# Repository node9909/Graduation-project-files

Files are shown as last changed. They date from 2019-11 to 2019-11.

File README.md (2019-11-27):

# Graduation internship report attachments (HD-SEMG system ADS1298)
 THis folder includes: Hardware files, software files, python application, MATLAB and report, design was to build a protable and wireless HD-SEMG aquisition system for my graduation internship of my electrical engineering degree at Hogeschool Rotterdam, the internship took place at Bio-engineering.pl in Wroclaw.

 The hypothesis of the project was ”Can the AMAC performance level be improved in direct controlled (DC) myoelectric systems by exactly locating the location where the patient has the most amount of cover the agonist and antagonist of the residual limb during different hand gestures’’. The goal was to develop a device that can be used to confirm this hypothesis, the could be achieved by measuring the muscle potentials over the residual limb during different hand gestures (HD-SEMG recording)

 In the project multiple AFE were designed were presented (based on AD8232 adn INA333), the function of the AFE to amplify and filter the EMG signal. THe EMG channels were digitezed using the ADS1298. the ADC data is read from the ADS1298 via an Arduino DUE (SAM3X8E)/ STM32F4.A PC application was developed to visualize the data and verifiy certain system specification (CMRR, IRN and Gain). The Current design is capable of measuring up to 1kSps with the Arduino DUE and to >4kSps with the STM32F411, the problem with the STM32F4 is the the Python application and realterm cannot open the USB port (CDC) to read the data, but it can be open in Tera term. If anybody knows why I would be happy to know :) 

 If you would like to continue this project Idea, feel to contact me for more info about the future improvements or any other questions about the design of the project.

# Contact details
 If you have any questions about the project feel free to contract me at: okersten@gmail.com

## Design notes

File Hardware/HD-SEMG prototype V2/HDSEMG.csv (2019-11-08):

Id | Designator | Behuizing | Hoeveelheid | Orientatie | Leverancier en ref
1 | REF** | KiCad-Logo2_8mm_SilkScreen | 1 | KiCad-Logo2_8mm_SilkScreen
2 | J26,J16,J15,J13,J14,J17,J24 | PinHeader_1x03_P2.54mm_Vertical | 7 | Conn_01x03
3 | GND1 | PinSocket_1x04_P2.54mm_Vertical | 1 | Conn_02x02_Counter_Clockwise
4 | J2 | PinSocket_1x04_P2.54mm_Vertical | 1 | Conn_01x04
5 | J3,J4,J5 | PinSocket_2x02_P2.54mm_Vertical | 3 | Conn_02x02_Counter_Clockwise
6 | J22,J25,J23,J21 | PinSocket_1x03_P2.54mm_Vertical | 4 | Conn_01x03
7 | J10,J9,CH8,CH7,CH6,CH5,CH4 | PinHeader_1x02_P2.54mm_Vertical | 7 | Conn_01x02
8 | J8,J7,J12 | PinHeader_1x01_P2.54mm_Vertical | 3 | Conn_01x01
9 | C54,C56,C55,C53,C52 | C_0805_2012Metric_Pad1.15x1.40mm_HandSolder | 5 | 10uF
10 | J30 | PinHeader_1x08_P2.54mm_Vertical | 1 | Conn_01x08
11 | JP6,JP3,JP1,JP5,JP8,JP9 | PinHeader_1x02_P2.54mm_Vertical | 6 | Jumper
12 | R118,R117,R22,R21,R39,R40 | R_0805_2012Metric_Pad1.15x1.40mm_HandSolder | 6 | 11k
13 | TP4,TP22,TP7,TP21,TP3,TP12,TP20,TP23,TP29,TP25,TP35,TP24,TP1,TP11,TP13,TP14,TP26,TP27,TP28,TP36,TP37,TP6 | keystone_PCB_TEST_PIN | 22 | 5003
14 | U15,U8,U33 | MSOP-8_3x3mm_P0.65mm | 3 | INA333AIDGKR
15 | U9,U35,U17 | VSSOP-8_3.0x3.0mm_P0.65mm | 3 | THS4521IDGKT
16 | R119,R120,R41,R24,R23,R42 | R_0805_2012Metric_Pad1.15x1.40mm_HandSolder | 6 | 50R
17 | U16,U34,U10 | SOT-23-5 | 3 | OPA333xxDBV
18 | R116,R115,R18,R37,R38,R19 | R_0805_2012Metric_Pad1.15x1.40mm_HandSolder | 6 | 5.6k
19 | C1 | C_0805_2012Metric_Pad1.15x1.40mm_HandSolder | 1 | 1M
20 | C4 | C_0805_2012Metric_Pad1.15x1.40mm_HandSolder | 1 | 47nF
21 | C5,C40,C112,C16,C22 | C_0805_2012Metric_Pad1.15x1.40mm_HandSolder | 5 | 4.7uF
22 | J1,J18 | MX387GL | 2 | AUDIO_JACK_By_OLIVER
23 | C6,C48,C120 | C_0805_2012Metric_Pad1.15x1.40mm_HandSolder | 3 | 220nF
24 | C7,C8,C14,C15,C114,C42,C46,C113,C45,C41,C118,C117 | C_0805_2012Metric_Pad1.15x1.40mm_HandSolder | 12 | 100n
25 | C12,C51,C123 | C_0805_2012Metric_Pad1.15x1.40mm_HandSolder | 3 | 33nF
26 | C9,C10,C50,C122 | C_0805_2012Metric_Pad1.15x1.40mm_HandSolder | 4 | 2.2nF
27 | C11,C13,C43,C44,C116,C115 | C_0805_2012Metric_Pad1.15x1.40mm_HandSolder | 6 | 100nF
28 | C49,C121 | C_0805_2012Metric_Pad1.15x1.40mm_HandSolder | 2 | 2.2n
29 | C47,C119 | C_0805_2012Metric_Pad1.15x1.40mm_HandSolder | 2 | 47n
30 | JP4,JP7 | SolderJumper-2_P1.3mm_Open_Pad1.0x1.5mm | 2 | Jumper
31 | R25,R34,R112 | R_0805_2012Metric_Pad1.15x1.40mm_HandSolder | 3 | 220k
32 | R14,R35,R15,R114,R36,R113 | R_0805_2012Metric_Pad1.15x1.40mm_HandSolder | 6 | 1.1k
33 | R17,R31,R108,R109,R16,R30 | R_0805_2012Metric_Pad1.15x1.40mm_HandSolder | 6 | 51k
34 | R20,R110,R32 | R_0805_2012Metric_Pad1.15x1.40mm_HandSolder | 3 | 4300R
35 | R2 | R_0805_2012Metric_Pad1.15x1.40mm_HandSolder | 1 | 1.5nF
36 | R33,R111 | R_0805_2012Metric_Pad1.15x1.40mm_HandSolder | 2 | 430k
37 | R26 | R_0805_2012Metric_Pad1.15x1.40mm_HandSolder | 1 | 110k
38 | R1,R28 | R_0805_2012Metric_Pad1.15x1.40mm_HandSolder | 2 | 100k
39 | TP5,TP2 | TPCW51D250H460P | 2 | 5003
40 | R10 | R_0805_2012Metric_Pad1.15x1.40mm_HandSolder | 1 | 0R
41 | R9,R6,R7 | R_0805_2012Metric_Pad1.15x1.40mm_HandSolder | 3 | 10k
42 | L5,L4,L3,L2 | L_0805_2012Metric_Pad1.15x1.40mm_HandSolder | 4 | INDUCTOR
43 | D1 | D_0805_2012Metric_Castellated | 1 | LED
44 | C2 | Fuse_1812_4532Metric_Pad1.30x3.40mm_HandSolder | 1 | 470pF
45 | C3 | C_1206_3216Metric_Pad1.42x1.75mm_HandSolder | 1 | 2.2uF
46 | C17,C18,C19,C21,C27,C29,C30,C31,C33,C39 | C_0805_2012Metric_Pad1.15x1.40mm_HandSolder | 10 | 1uF
47 | C23,C25,C20 | C_0805_2012Metric_Pad1.15x1.40mm_HandSolder | 3 | 2.2uF
48 | C24,C124 | C_0805_2012Metric_Pad1.15x1.40mm_HandSolder | 2 | 10nF
49 | C26,C28 | C_1206_3216Metric_Pad1.42x1.75mm_HandSolder | 2 | 0.1uF
50 | C32 | C_0805_2012Metric_Pad1.15x1.40mm_HandSolder | 1 | .1uF
51 | C34 | C_0805_2012Metric_Pad1.15x1.40mm_HandSolder | 1 | 22uF
52 | C35 | C_1206_3216Metric | 1 | 10uF
53 | C36 | C_0805_2012Metric_Pad1.15x1.40mm_HandSolder | 1 | 0.1u
54 | C37 | C_0805_2012Metric_Pad1.15x1.40mm_HandSolder | 1 | 1nF
55 | C38 | C_0805_2012Metric_Pad1.15x1.40mm_HandSolder | 1 | 0.1uF
56 | F1 | Fuse_1206_3216Metric_Pad1.42x1.75mm_HandSolder | 1 | Fuse
57 | IC1 | TQFP-64_10x10mm_P0.5mm | 1 | ADS1298_By_Oliver
58 | Power_In1,J31 | TerminalBlock_bornier-2_P5.08mm | 2 | Screw_Terminal_01x02
59 | J11 | BarrelJack_Horizontal | 1 | Barrel_Jack_Switch
60 | L1 | L_Bourns_SRN6045TA | 1 | 10uH
61 | PS1 | CONV_R2S-1205 | 1 | R2S-1205
62 | R3,R4,R5 | R_0805_2012Metric_Pad1.15x1.40mm_HandSolder | 3 | 10K
63 | U11 | SOT-223-3_TabPin2 | 1 | TLV1117-25
64 | U12 | SOT-223-3_TabPin2 | 1 | MCP1825S
65 | U14 | SOT-23-5_HandSoldering | 1 | TPS72325
66 | U36 | SOIC254P1016X460-5N | 1 | 357LB3CI002M0480
67 | R8 | R_0805_2012Metric_Pad1.15x1.40mm_HandSolder | 1 | 50k
68 | U13 | SOIC127P600X175-8N | 1 | MAX889TESA+
69 | U2,U3 | SOIC-16_3.9x9.9mm_P1.27mm | 2 | Si8663
70 | J19 | PinHeader_1x06_P2.54mm_Vertical | 1 | Conn_01x06

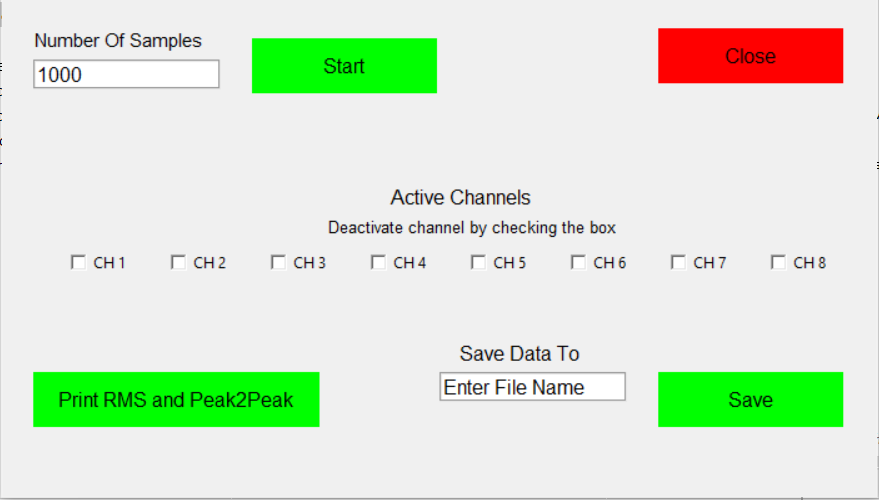
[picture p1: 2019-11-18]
PC Application/app.PNG

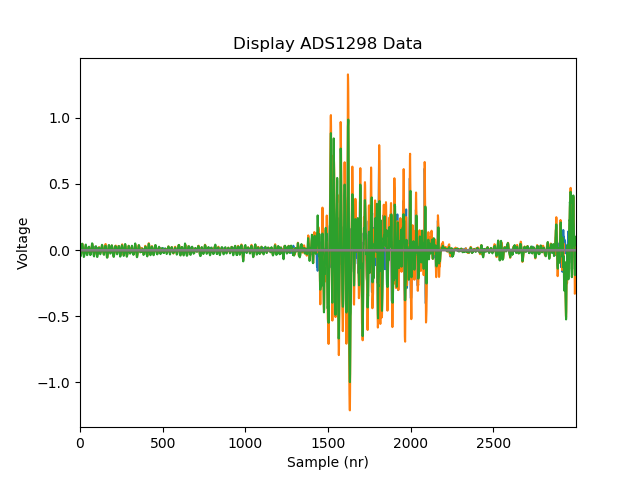
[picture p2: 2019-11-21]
PC Application/realtest.png

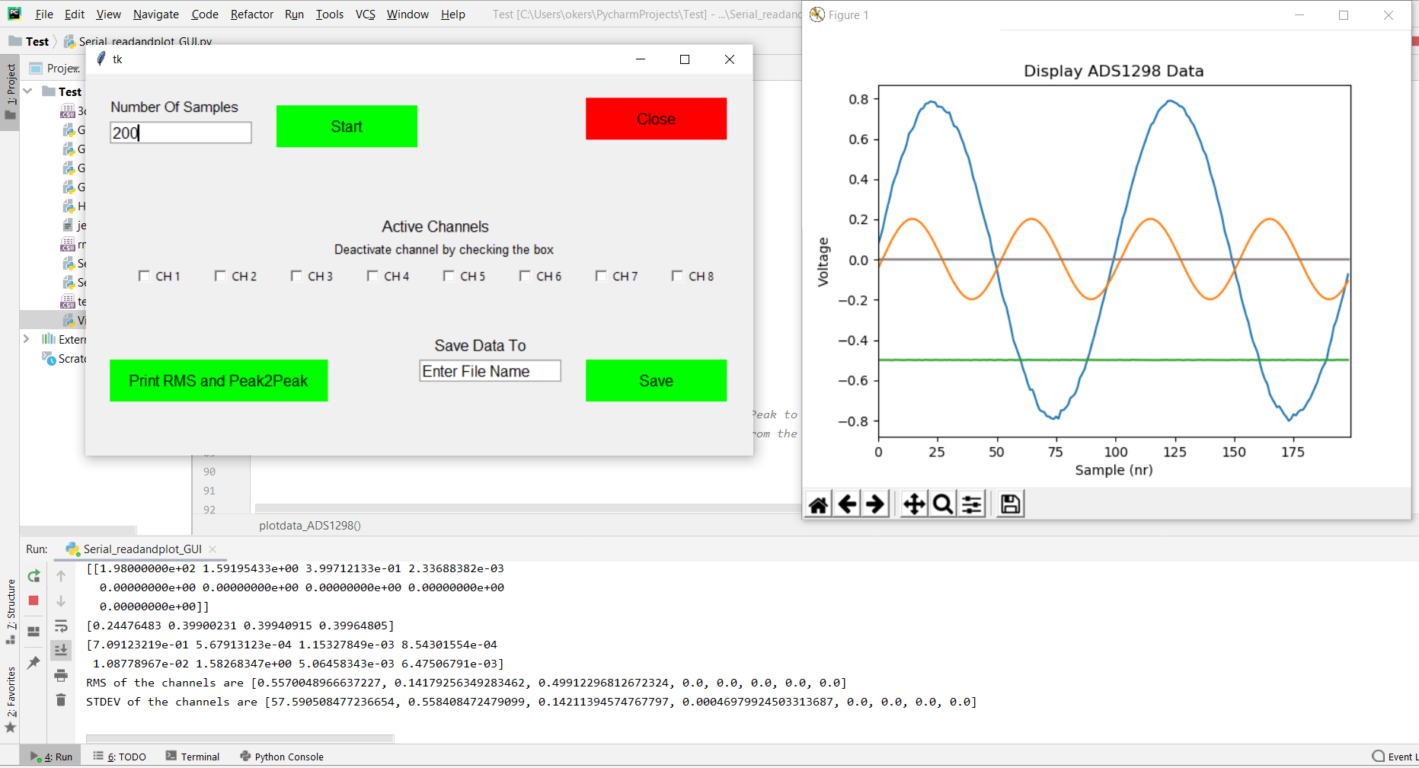
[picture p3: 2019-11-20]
PC Application/rmstest.PNG

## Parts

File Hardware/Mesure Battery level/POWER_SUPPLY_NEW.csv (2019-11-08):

Reference | Value | Footprint | Datasheet | Veld4 | Veld5 | Veld7 | Veld8
U4 | MCP73831 | Package_TO_SOT_SMD:SOT-23-5 |  | IC-09995
D2 | bat charging | LED_SMD:LED_0805_2012Metric_Pad1.15x1.40mm_HandSolder | ~
D3 | battery full | LED_SMD:LED_0805_2012Metric_Pad1.15x1.40mm_HandSolder | ~
R4 | 1K | Resistor_SMD:R_0805_2012Metric_Pad1.15x1.40mm_HandSolder | ~
R5 | 1K | Resistor_SMD:R_0805_2012Metric_Pad1.15x1.40mm_HandSolder | ~
R10 | Charge Current | Resistor_SMD:R_0805_2012Metric_Pad1.15x1.40mm_HandSolder | ~
C3 | 10uF | Capacitor_SMD:C_0805_2012Metric_Pad1.15x1.40mm_HandSolder | ~
J3 | CONN_02JST-PTH-2 | Connector_JST:JST_PH_S2B-PH-K_1x02_P2.00mm_Horizontal |  | CONN-09863
C4 | 10uF | Capacitor_SMD:C_0805_2012Metric_Pad1.15x1.40mm_HandSolder | ~
U5 | TPS61090 | Package_DFN_QFN:QFN-16-1EP_4x4mm_P0.65mm_EP2.5x2.5mm | http://www.ti.com/lit/ds/symlink/tps61090.pdf
L1 | 6.8uH | Inductor_SMD:L_Bourns_SRN6045TA | ~
C5 | 10uF | Capacitor_SMD:C_0805_2012Metric_Pad1.15x1.40mm_HandSolder | ~
C6 | 0.1uF | Capacitor_SMD:C_0805_2012Metric_Pad1.15x1.40mm_HandSolder | ~
R12 | 1.8MR | Resistor_SMD:R_0805_2012Metric_Pad1.15x1.40mm_HandSolder | ~
R11 | R | Resistor_SMD:R_0805_2012Metric_Pad1.15x1.40mm_HandSolder | ~
R13 | 330k | Resistor_SMD:R_0805_2012Metric_Pad1.15x1.40mm_HandSolder | ~
R17 | 1.8Mohm | Resistor_SMD:R_0805_2012Metric_Pad1.15x1.40mm_HandSolder | ~
R18 | 200k | Resistor_SMD:R_0805_2012Metric_Pad1.15x1.40mm_HandSolder | ~
R16 | 2MOhm | Resistor_SMD:R_0805_2012Metric_Pad1.15x1.40mm_HandSolder | ~
C11 | 2.2uF | Capacitor_SMD:C_0805_2012Metric_Pad1.15x1.40mm_HandSolder | ~
J7 | POWER_OUT | Connector_JST:JST_PH_S2B-PH-K_1x02_P2.00mm_Horizontal |  | CONN-09863
C12 | 100UF(tan) | Capacitor_Tantalum_SMD:CP_EIA-3528-12_Kemet-T_Pad1.50x2.35mm_HandSolder | ~
SW1 | Switch_SW_SPDT | Connector_PinSocket_2.54mm:PinSocket_1x03_P2.54mm_Vertical
D7 | LED | LED_SMD:LED_0805_2012Metric_Pad1.15x1.40mm_HandSolder | ~
R21 | 1K | Resistor_SMD:R_0805_2012Metric_Pad1.15x1.40mm_HandSolder | ~
U7 | ATtiny85-20PU | Package_DIP:DIP-8_W7.62mm | http://ww1.microchip.com/downloads/en/DeviceDoc/atmel-2586-avr-8-bit-microcontroller-attiny25-attiny45-attiny85_datasheet.pdf
J6 | AVR-ISP-6 | Connector_PinSocket_2.54mm:PinSocket_2x03_P2.54mm_Vertical | ~
D6 | LED_AT | LED_SMD:LED_0805_2012Metric_Pad1.15x1.40mm_HandSolder | ~
R14 | 1K | Resistor_SMD:R_0805_2012Metric_Pad1.15x1.40mm_HandSolder | ~
U6 | MCP1703A-3302_SOT23 | Package_TO_SOT_SMD:SOT-23 | http://ww1.microchip.com/downloads/en/DeviceDoc/20005122B.pdf
C9 | 1uF | Capacitor_SMD:C_0805_2012Metric_Pad1.15x1.40mm_HandSolder | ~
C10 | 1uF | Capacitor_SMD:C_0805_2012Metric_Pad1.15x1.40mm_HandSolder | ~
R15 | 10K | Resistor_SMD:R_0805_2012Metric_Pad1.15x1.40mm_HandSolder | ~
Y1 | Crystal | Crystal:Crystal_HC49-U_Vertical | ~
C8 | 22p | Capacitor_SMD:C_0805_2012Metric_Pad1.15x1.40mm_HandSolder | ~
C7 | 22p | Capacitor_SMD:C_0805_2012Metric_Pad1.15x1.40mm_HandSolder | ~
R19 | 4.7K | Resistor_SMD:R_0805_2012Metric_Pad1.15x1.40mm_HandSolder | ~
R20 | 4.7K | Resistor_SMD:R_0805_2012Metric_Pad1.15x1.40mm_HandSolder | ~
J5 | CONN_02JST-PTH-2 | Connector_JST:JST_PH_S2B-PH-K_1x02_P2.00mm_Horizontal |  | CONN-09863
J10 | GND | TestPoint:TestPoint_Pad_4.0x4.0mm |  | XXX-00000
J9 | 5V | TestPoint:TestPoint_Pad_4.0x4.0mm |  | XXX-00000
J11 | Conn_01x03 | Connector_PinSocket_2.54mm:PinSocket_1x03_P2.54mm_Vertical | ~
J1 | USB4065-XX-X_REVA | USB4065-XX-X_REVA:GCT_USB4065-XX-X_REVA | Global Connector Technology | None | USB4065-XX-X | Unavailable | None
JP1 | Jumper_3_Open | Jumper:SolderJumper-3_P1.3mm_Open_RoundedPad1.0x1.5mm | ~
J2 | Conn_02x04_Odd_Even | Connector_PinSocket_2.54mm:PinSocket_2x04_P2.54mm_Vertical | ~

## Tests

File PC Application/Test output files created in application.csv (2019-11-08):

0.000000000000000000e+00 | -1.533971969362731835e-01 | 9.966572042294983280e-01 | 0.000000000000000000e+00 | 0.000000000000000000e+00 | 0.000000000000000000e+00 | 0.000000000000000000e+00 | 0.000000000000000000e+00 | 0.000000000000000000e+00
1.000000000000000000e+00 | -1.284871254547984010e-01 | 9.967693563424773195e-01 | 0.000000000000000000e+00 | 0.000000000000000000e+00 | 0.000000000000000000e+00 | 0.000000000000000000e+00 | 0.000000000000000000e+00 | 0.000000000000000000e+00
2.000000000000000000e+00 | -1.160047669416388177e-01 | 9.967327352443616784e-01 | 0.000000000000000000e+00 | 0.000000000000000000e+00 | 0.000000000000000000e+00 | 0.000000000000000000e+00 | 0.000000000000000000e+00 | 0.000000000000000000e+00
3.000000000000000000e+00 | -9.101115358008785017e-02 | 9.968174215337539668e-01 | 0.000000000000000000e+00 | 0.000000000000000000e+00 | 0.000000000000000000e+00 | 0.000000000000000000e+00 | 0.000000000000000000e+00 | 0.000000000000000000e+00
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

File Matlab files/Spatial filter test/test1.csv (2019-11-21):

0.000000000000000000e+00 | 2.745151847022992038e-03 | -1.107559336132924073e-02 | -1.735038964156980848e-02 | 0.000000000000000000e+00 | 0.000000000000000000e+00 | 0.000000000000000000e+00 | 0.000000000000000000e+00 | 0.000000000000000000e+00
1.000000000000000000e+00 | 5.869103177678963203e-03 | -1.934938661448796018e-02 | -2.887316094316970741e-02 | 0.000000000000000000e+00 | 0.000000000000000000e+00 | 0.000000000000000000e+00 | 0.000000000000000000e+00 | 0.000000000000000000e+00
2.000000000000000000e+00 | 7.285595808696245998e-03 | -2.618809058524257730e-02 | -3.593845795851444841e-02 | 0.000000000000000000e+00 | 0.000000000000000000e+00 | 0.000000000000000000e+00 | 0.000000000000000000e+00 | 0.000000000000000000e+00
3.000000000000000000e+00 | 8.956147307890332393e-03 | -2.778339717190232011e-02 | -3.733263460786755139e-02 | 0.000000000000000000e+00 | 0.000000000000000000e+00 | 0.000000000000000000e+00 | 0.000000000000000000e+00 | 0.000000000000000000e+00
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

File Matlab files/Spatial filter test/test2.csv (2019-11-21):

0.000000000000000000e+00 | 1.794433807663179184e-03 | -1.213646079736480522e-03 | -4.971600171518346031e-03 | 0.000000000000000000e+00 | 0.000000000000000000e+00 | 0.000000000000000000e+00 | 0.000000000000000000e+00 | 0.000000000000000000e+00
1.000000000000000000e+00 | 3.414345194619321146e-03 | -1.819610812617636960e-03 | -7.287312422670414076e-03 | 0.000000000000000000e+00 | 0.000000000000000000e+00 | 0.000000000000000000e+00 | 0.000000000000000000e+00 | 0.000000000000000000e+00
2.000000000000000000e+00 | 5.646515565695234100e-03 | 5.461407358814162998e-03 | -2.397251414925028346e-03 | 0.000000000000000000e+00 | 0.000000000000000000e+00 | 0.000000000000000000e+00 | 0.000000000000000000e+00 | 0.000000000000000000e+00
3.000000000000000000e+00 | 6.628990963577147295e-03 | 1.012086988936303743e-02 | 1.074600347828906510e-03 | 0.000000000000000000e+00 | 0.000000000000000000e+00 | 0.000000000000000000e+00 | 0.000000000000000000e+00 | 0.000000000000000000e+00
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

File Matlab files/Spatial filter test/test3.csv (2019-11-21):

0.000000000000000000e+00 | 4.312420405437994778e-03 | 1.605720711436356418e-02 | 8.705807769990893397e-03 | 0.000000000000000000e+00 | 0.000000000000000000e+00 | 0.000000000000000000e+00 | 0.000000000000000000e+00 | 0.000000000000000000e+00
1.000000000000000000e+00 | 2.191543840353946809e-04 | 1.097517144384043720e-02 | 7.079029927138081289e-03 | 0.000000000000000000e+00 | 0.000000000000000000e+00 | 0.000000000000000000e+00 | 0.000000000000000000e+00 | 0.000000000000000000e+00
2.000000000000000000e+00 | -4.700661265928895950e-04 | 9.714604582143375119e-03 | 7.375145837681989364e-03 | 0.000000000000000000e+00 | 0.000000000000000000e+00 | 0.000000000000000000e+00 | 0.000000000000000000e+00 | 0.000000000000000000e+00
3.000000000000000000e+00 | -4.368782564256496761e-04 | 6.930542818372585449e-03 | 5.496025740626542602e-03 | 0.000000000000000000e+00 | 0.000000000000000000e+00 | 0.000000000000000000e+00 | 0.000000000000000000e+00 | 0.000000000000000000e+00
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

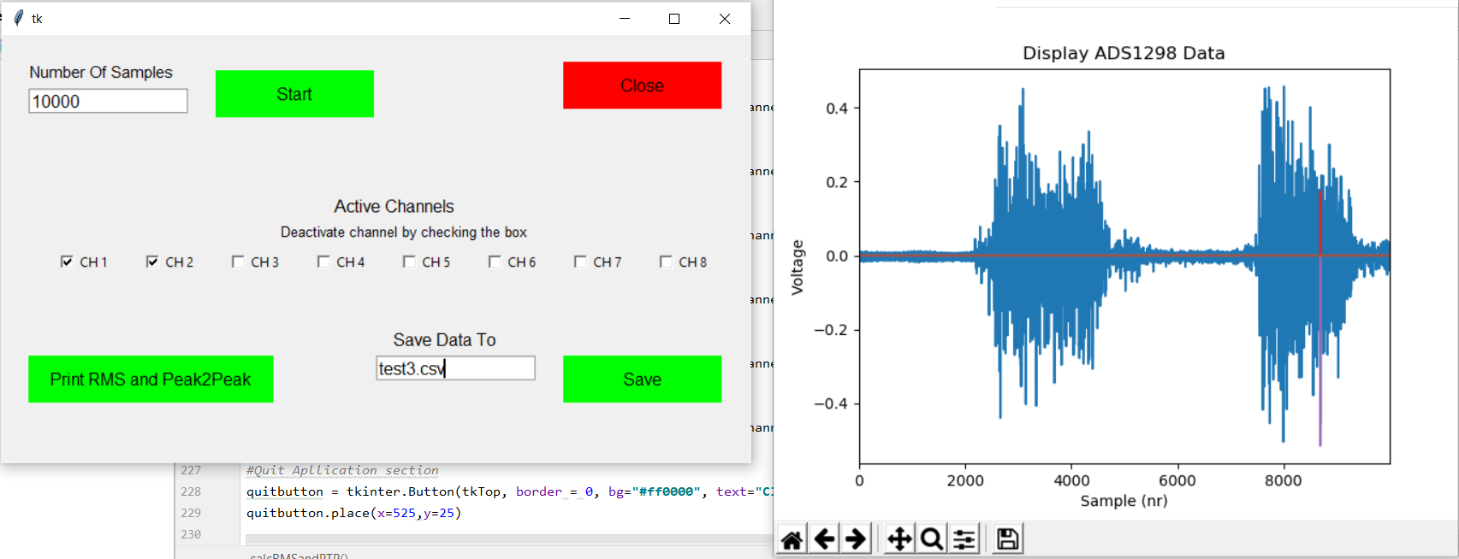
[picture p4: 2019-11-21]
PC Application/test4.PNG

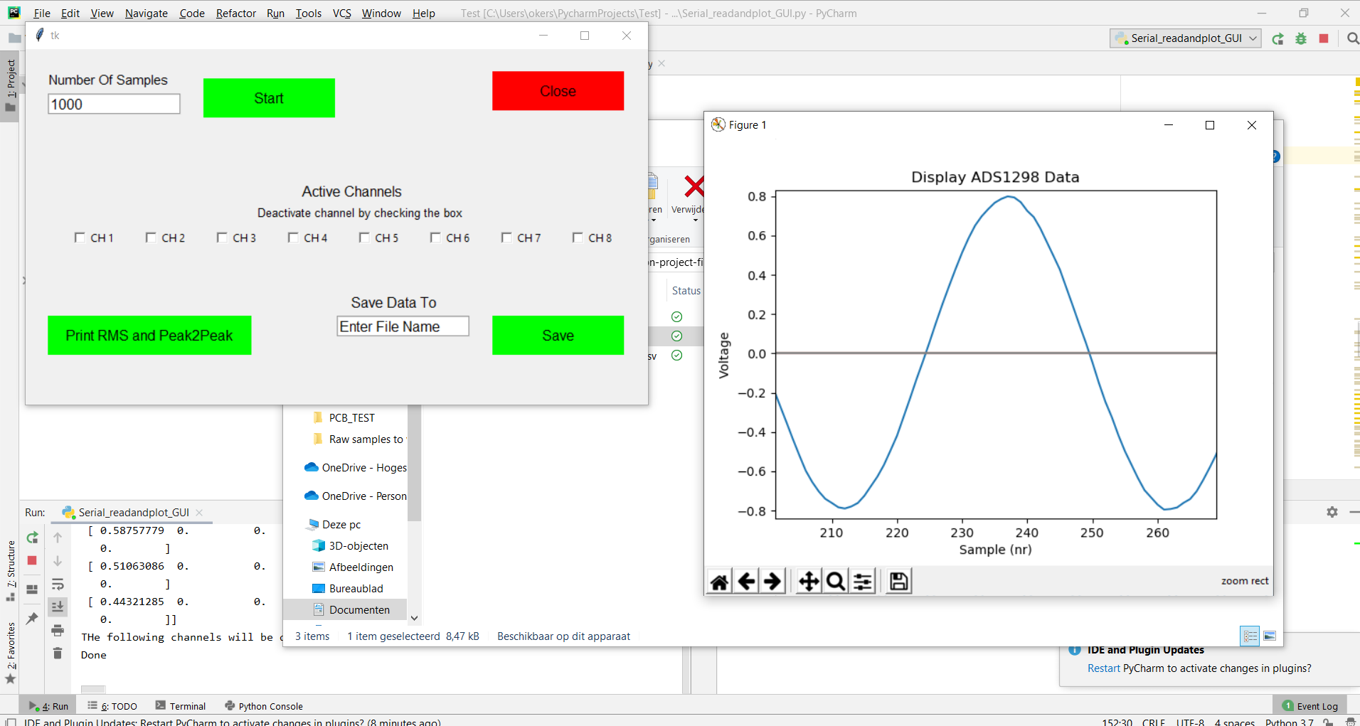
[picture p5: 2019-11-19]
PC Application/test.PNG

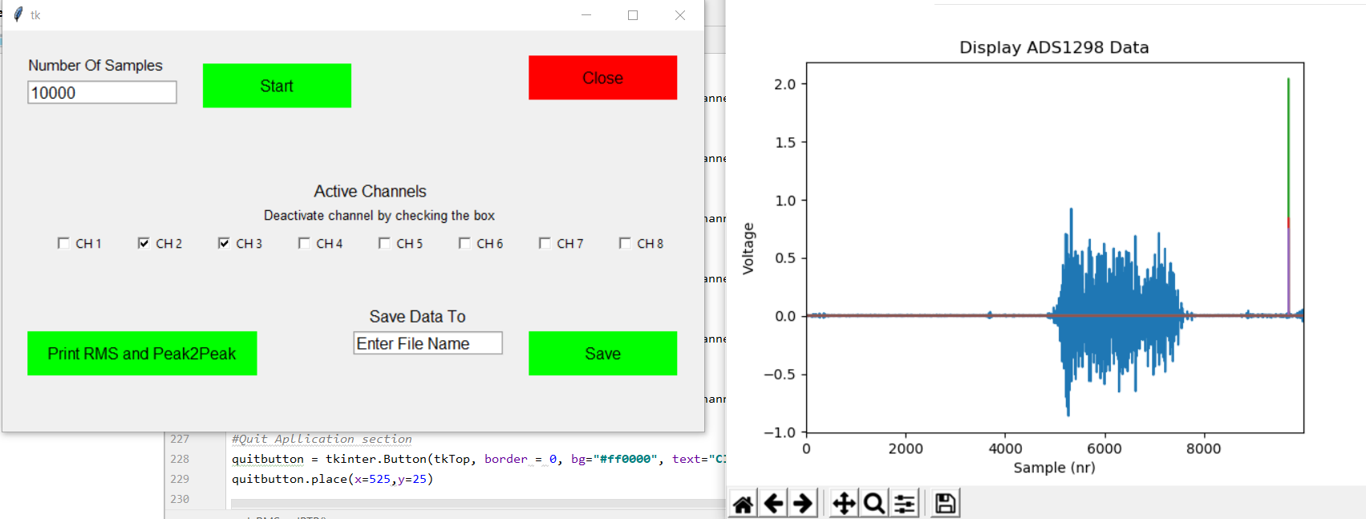
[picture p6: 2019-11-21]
PC Application/test3.PNG

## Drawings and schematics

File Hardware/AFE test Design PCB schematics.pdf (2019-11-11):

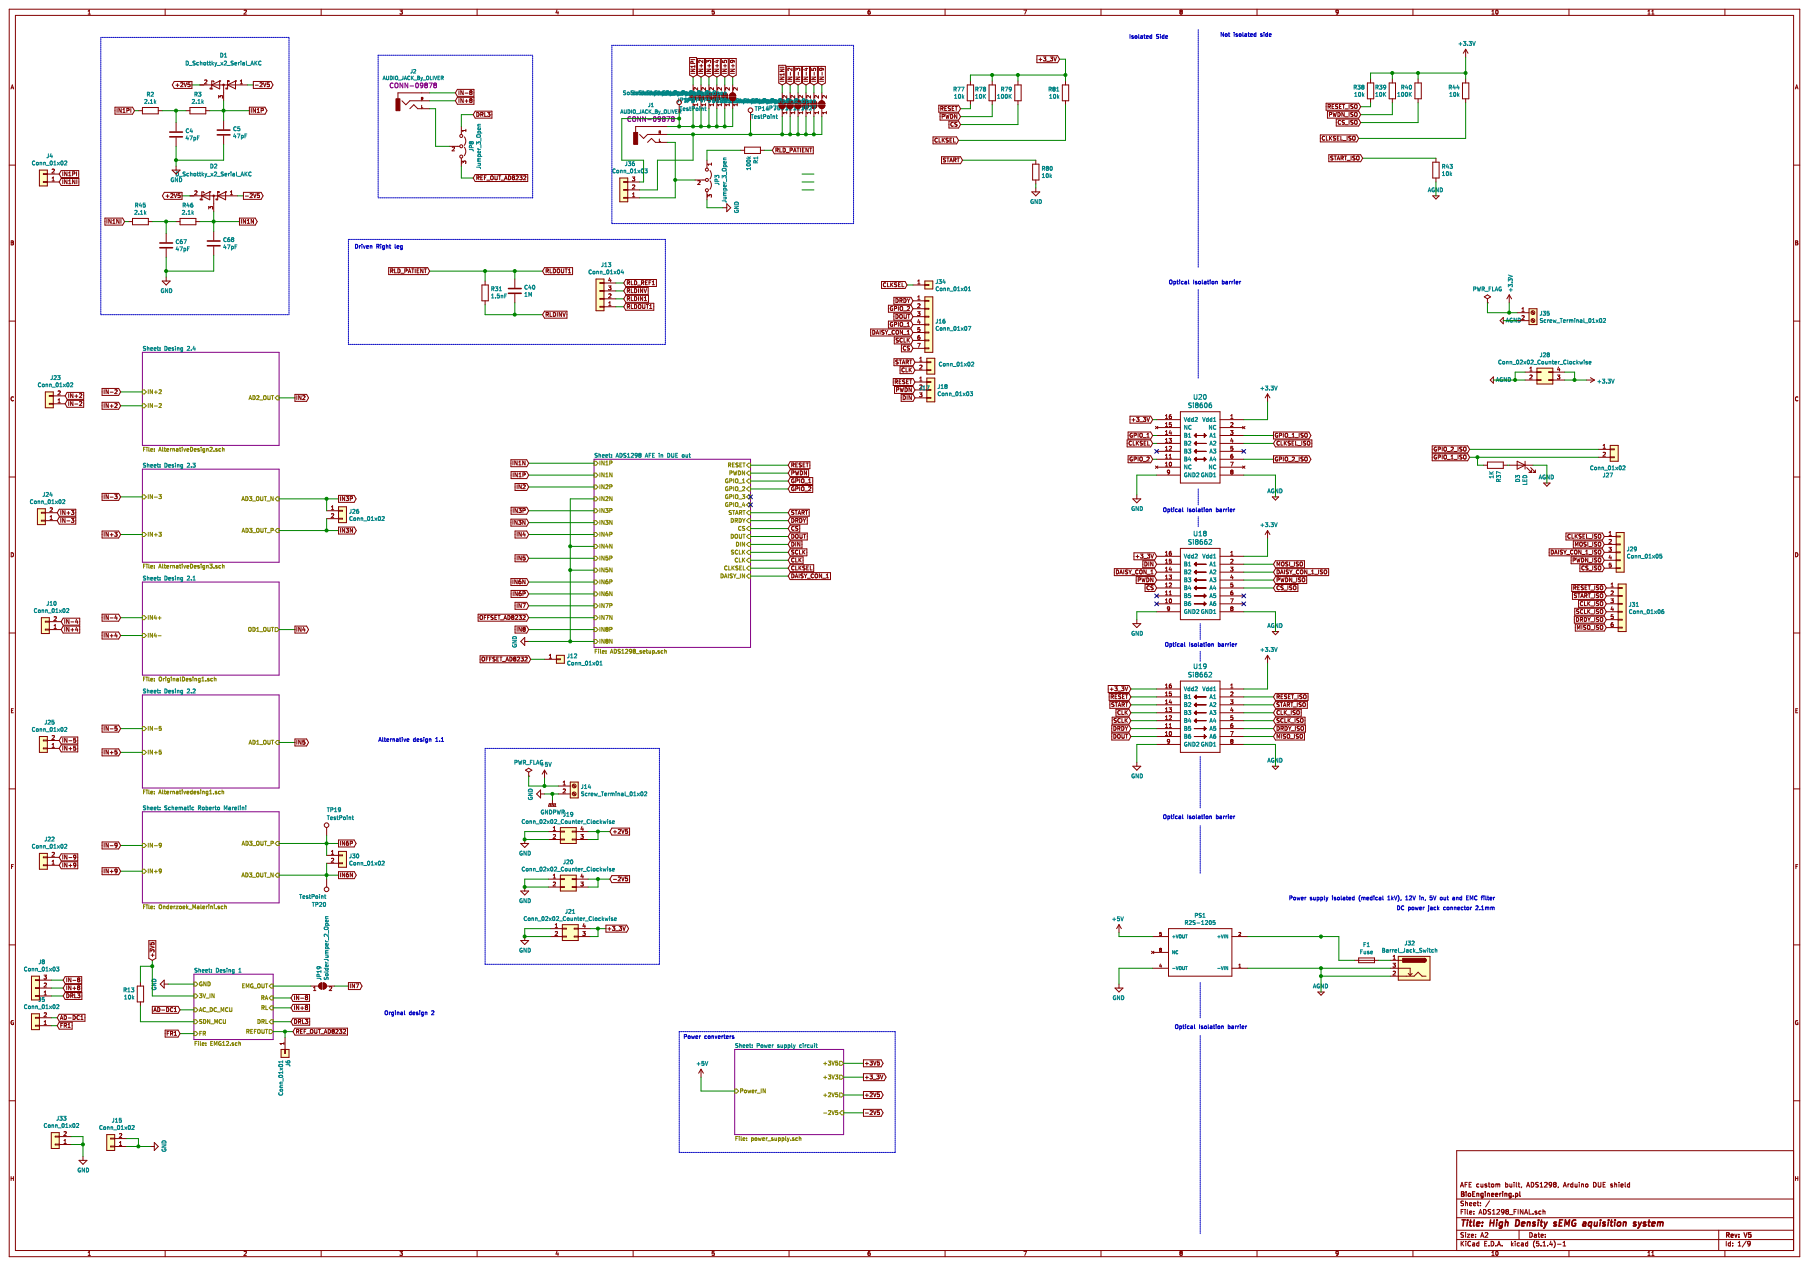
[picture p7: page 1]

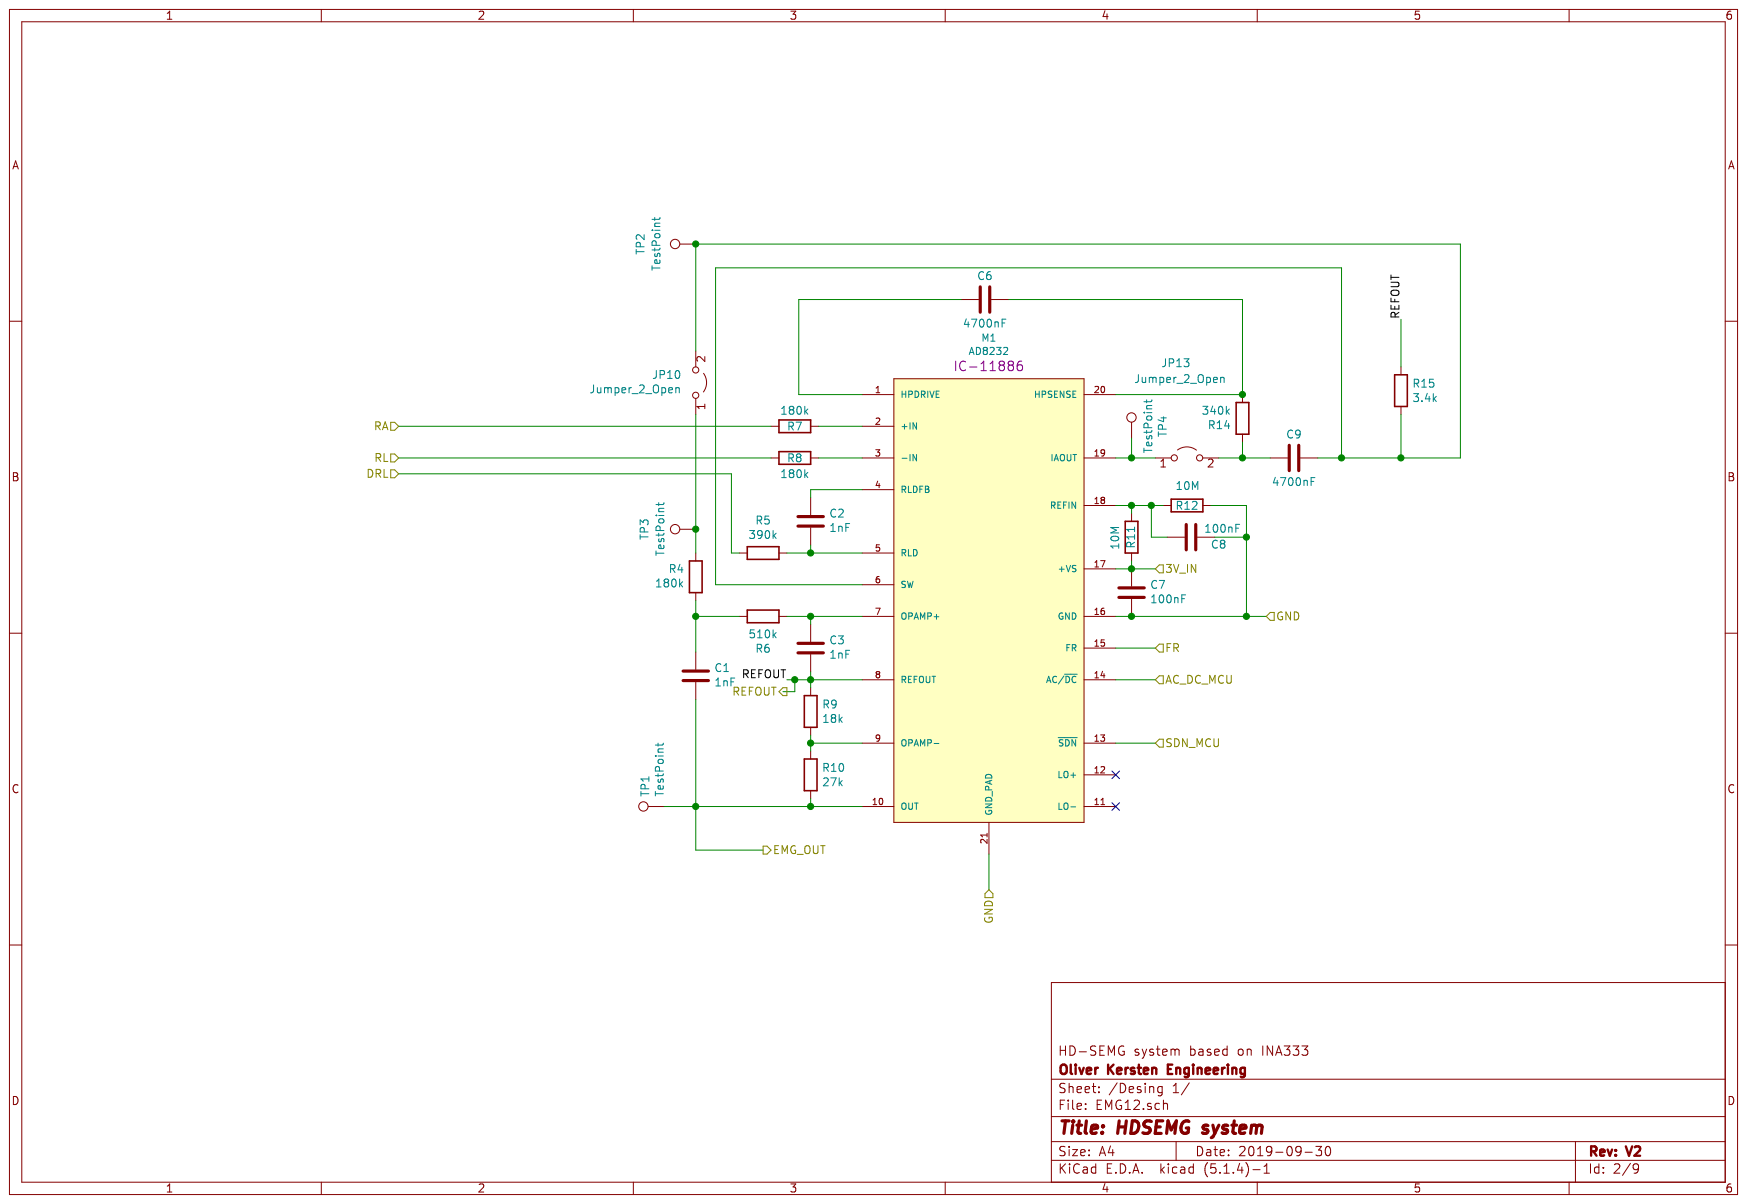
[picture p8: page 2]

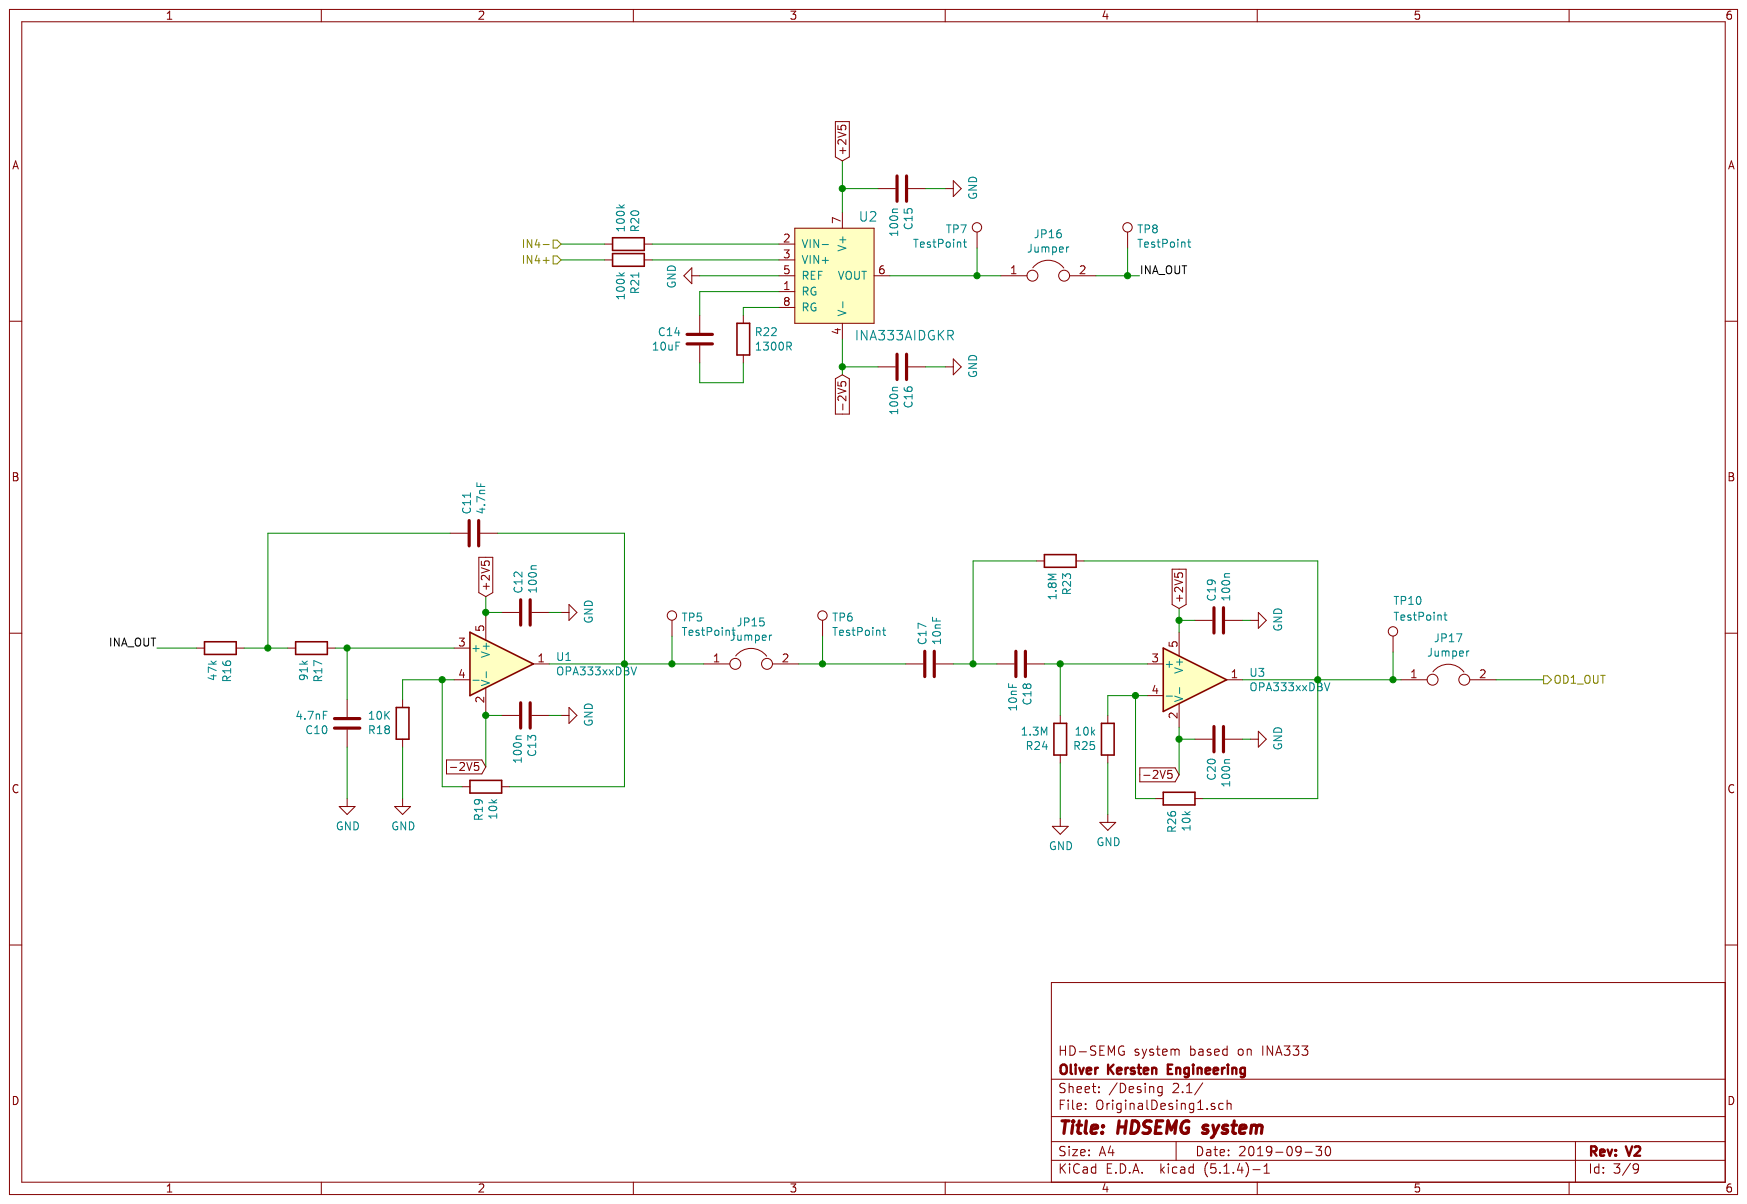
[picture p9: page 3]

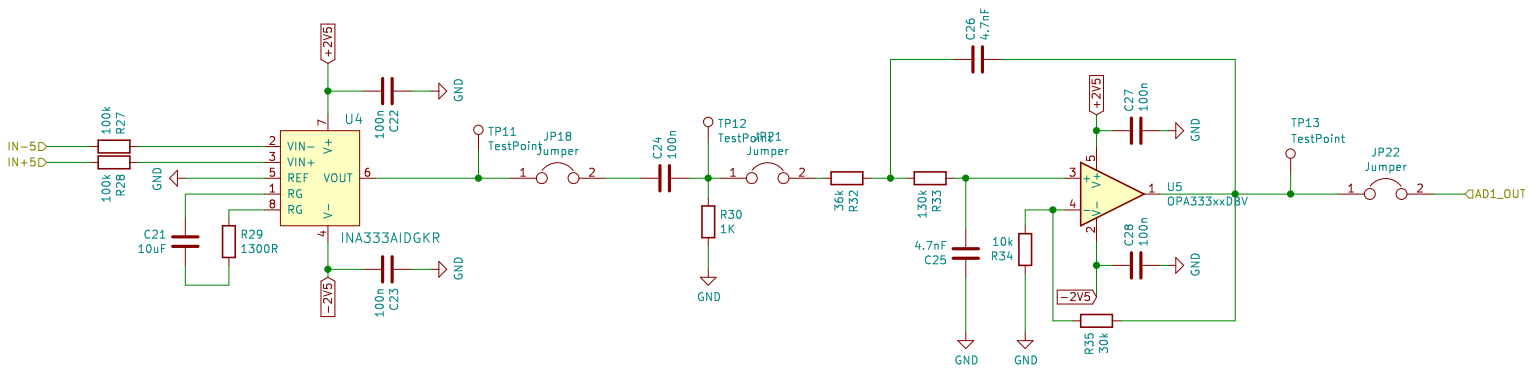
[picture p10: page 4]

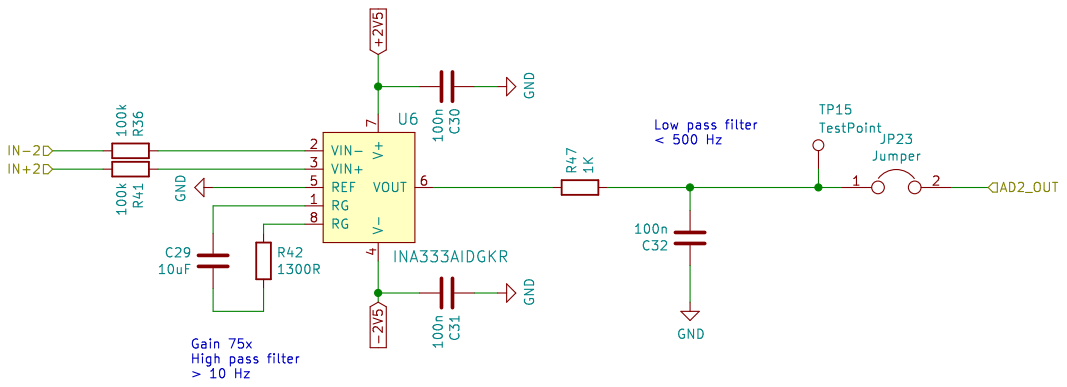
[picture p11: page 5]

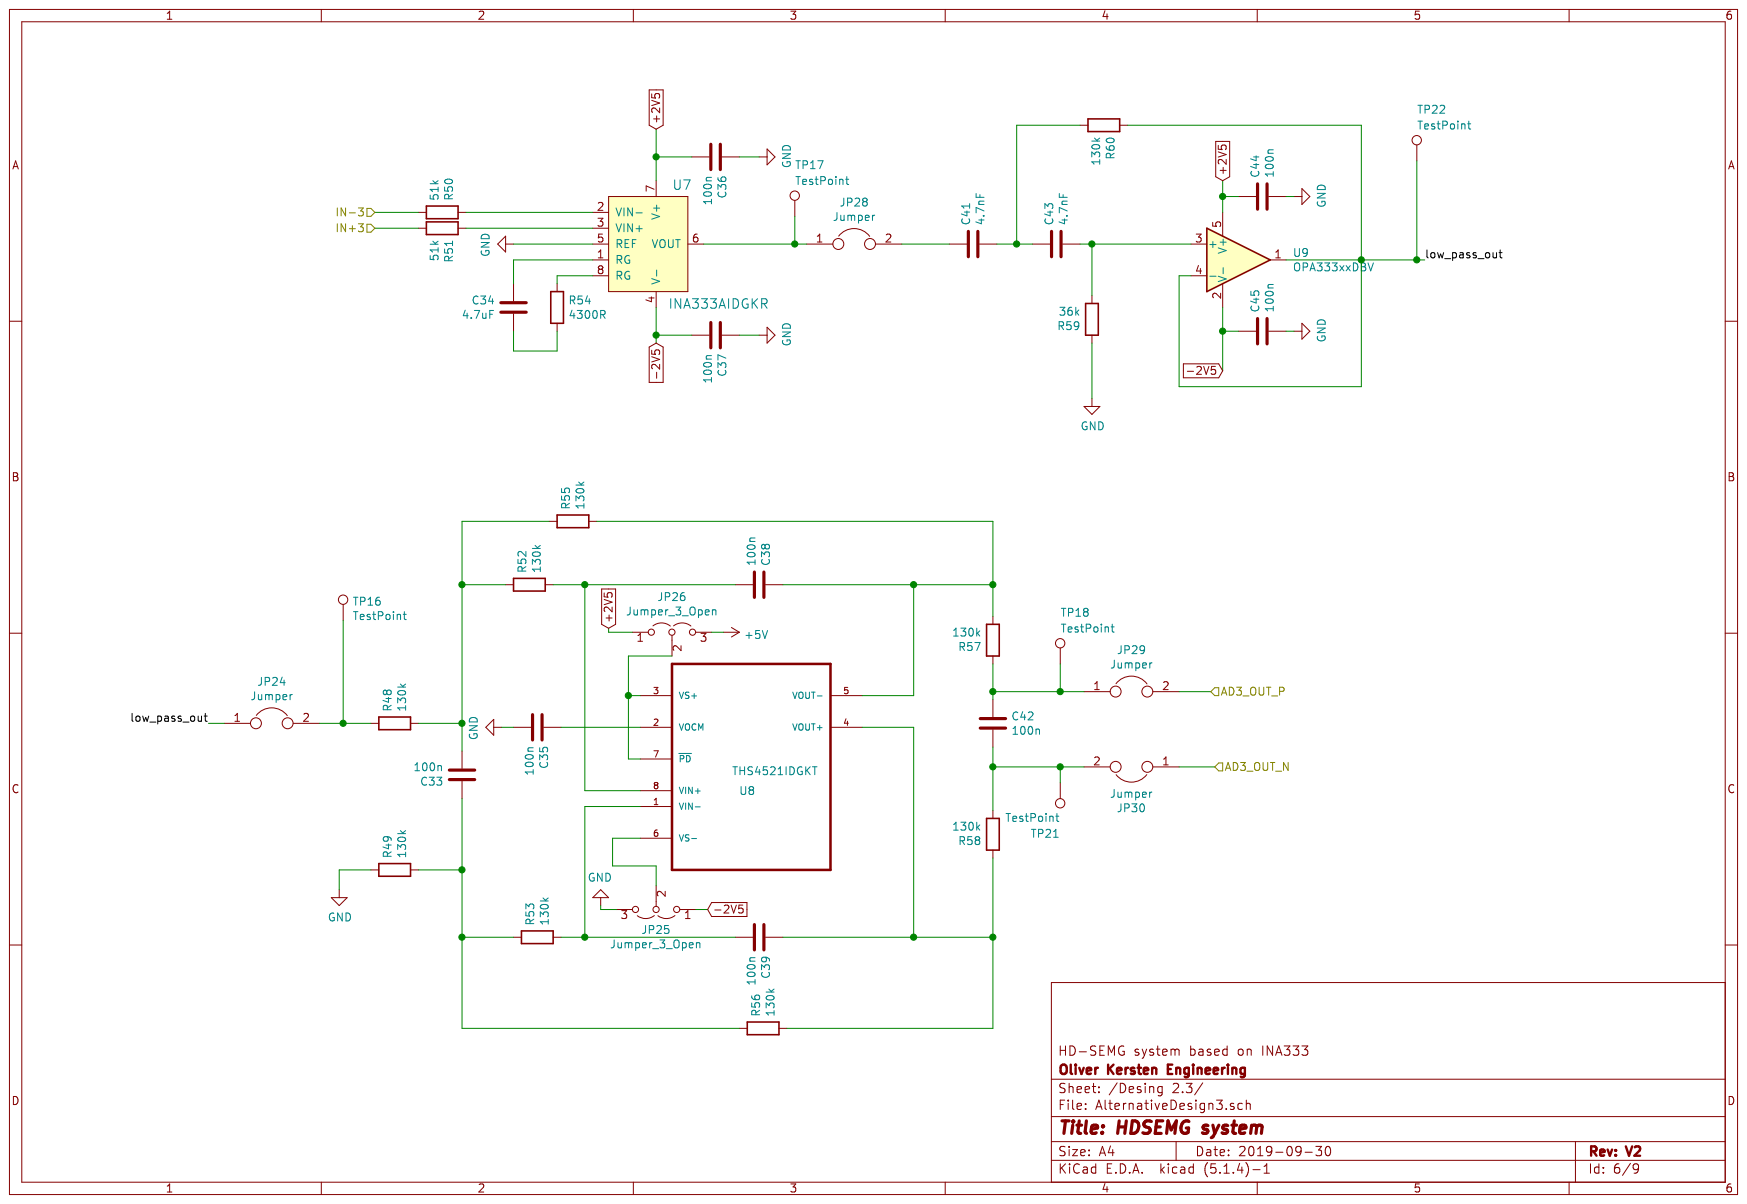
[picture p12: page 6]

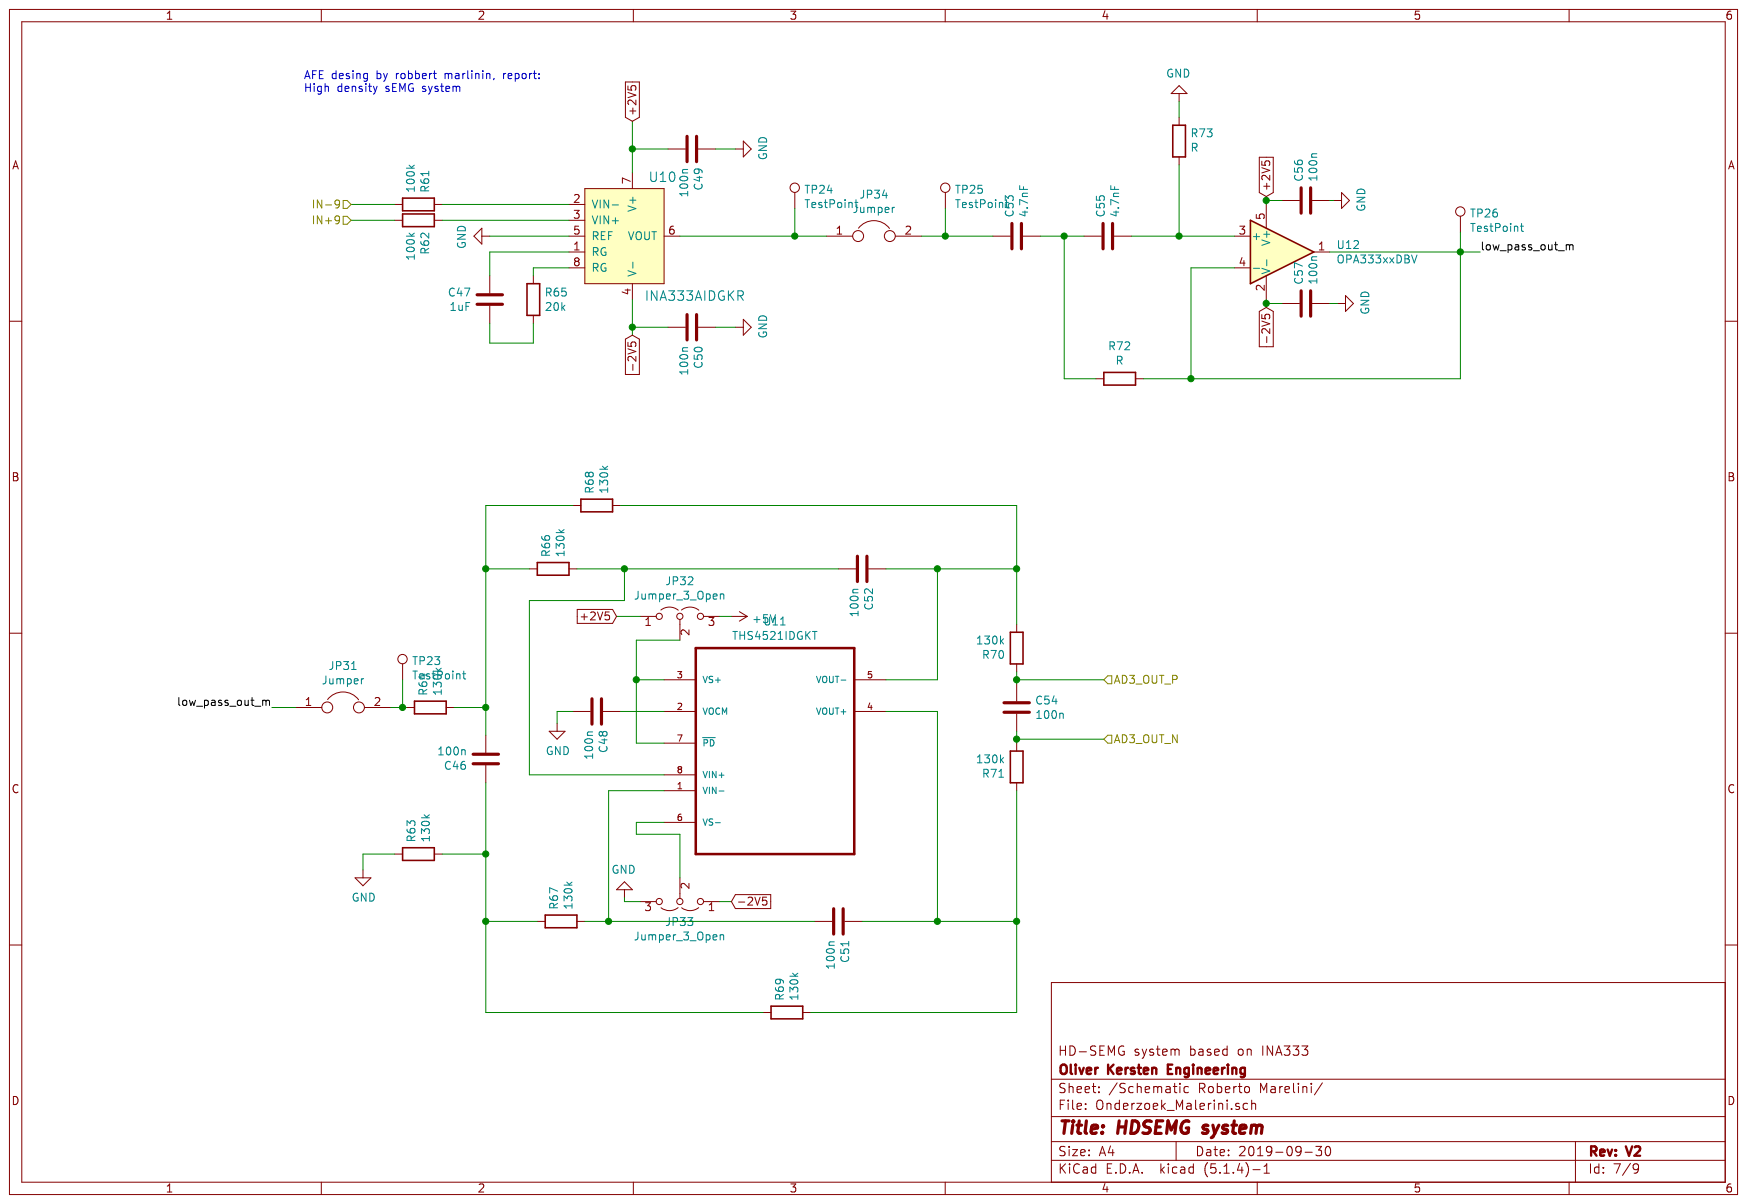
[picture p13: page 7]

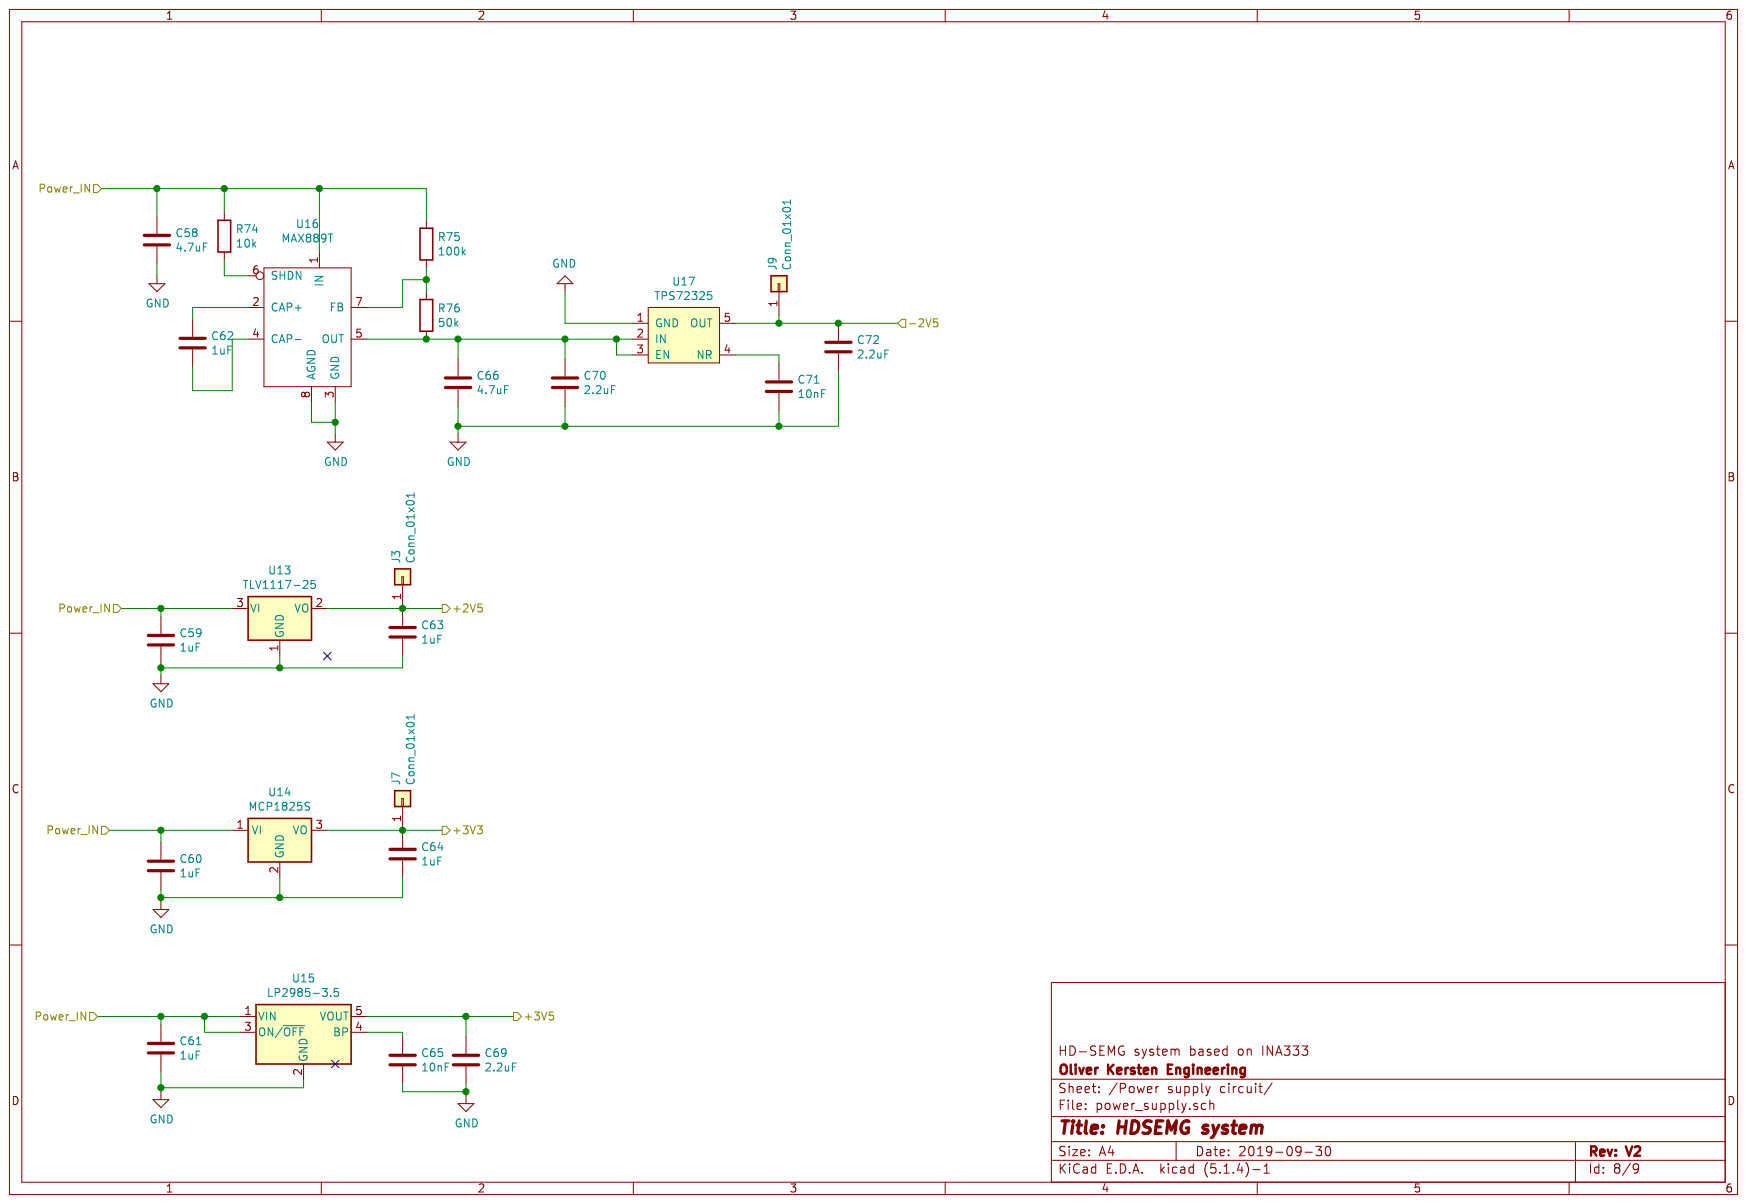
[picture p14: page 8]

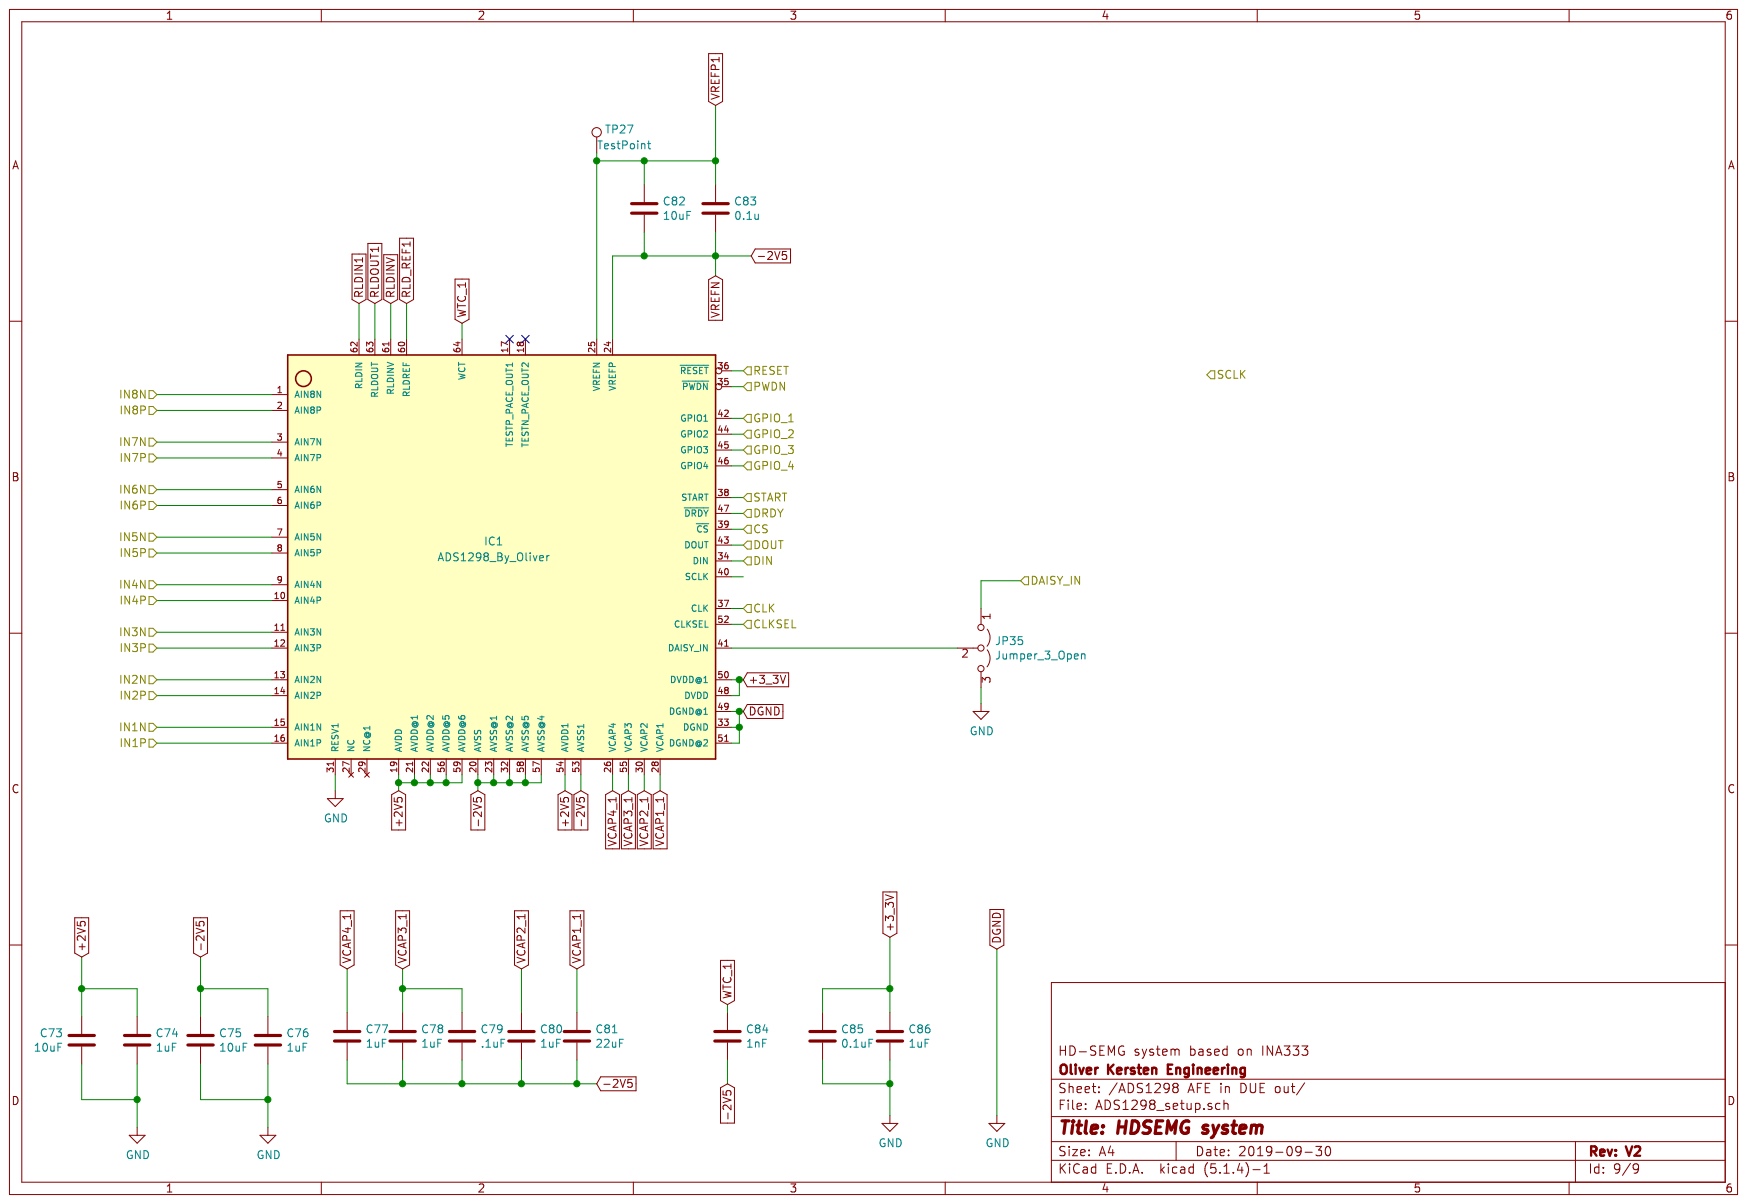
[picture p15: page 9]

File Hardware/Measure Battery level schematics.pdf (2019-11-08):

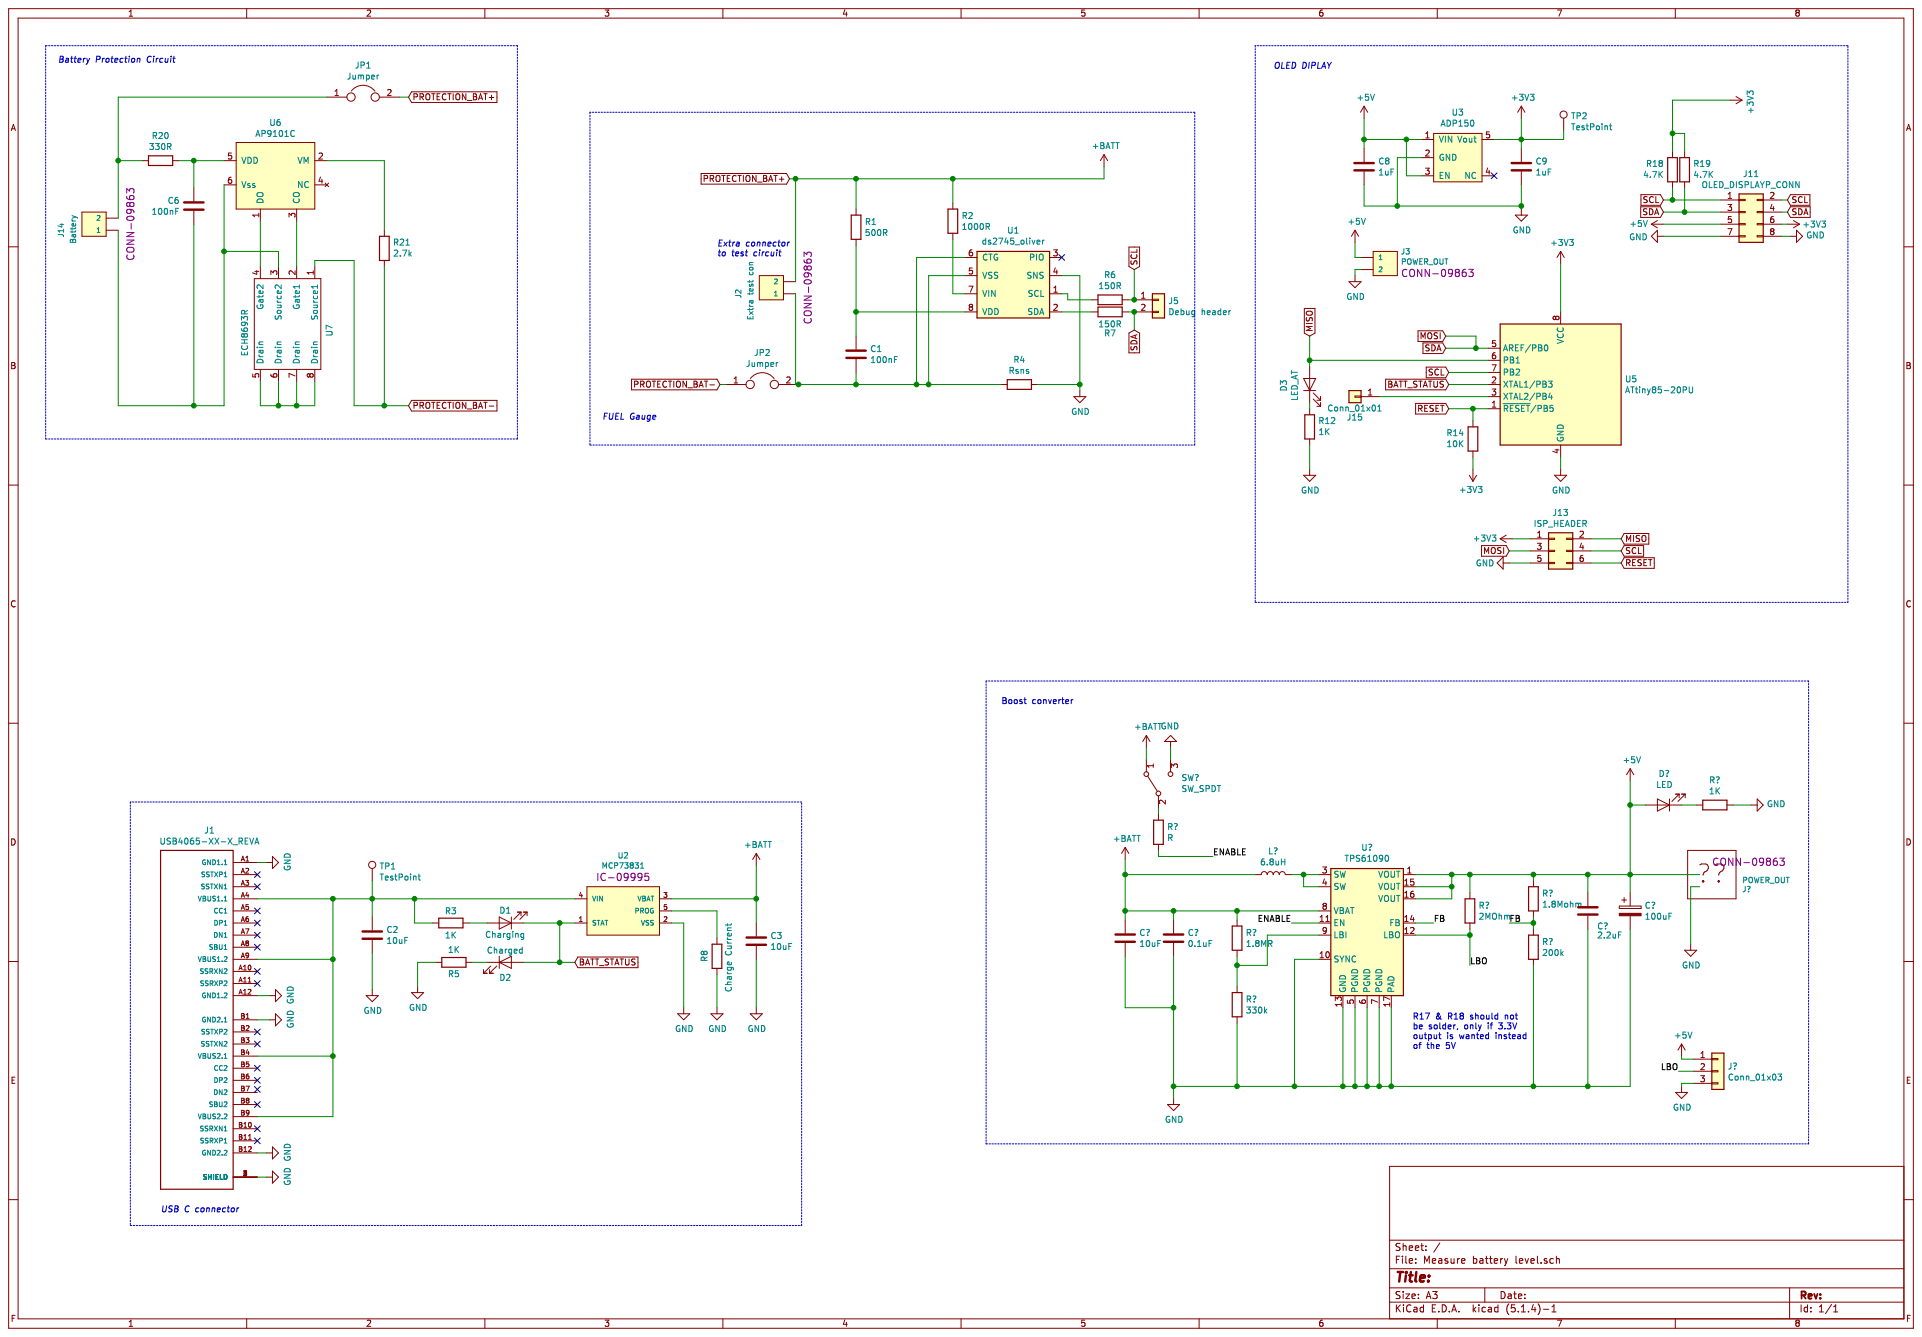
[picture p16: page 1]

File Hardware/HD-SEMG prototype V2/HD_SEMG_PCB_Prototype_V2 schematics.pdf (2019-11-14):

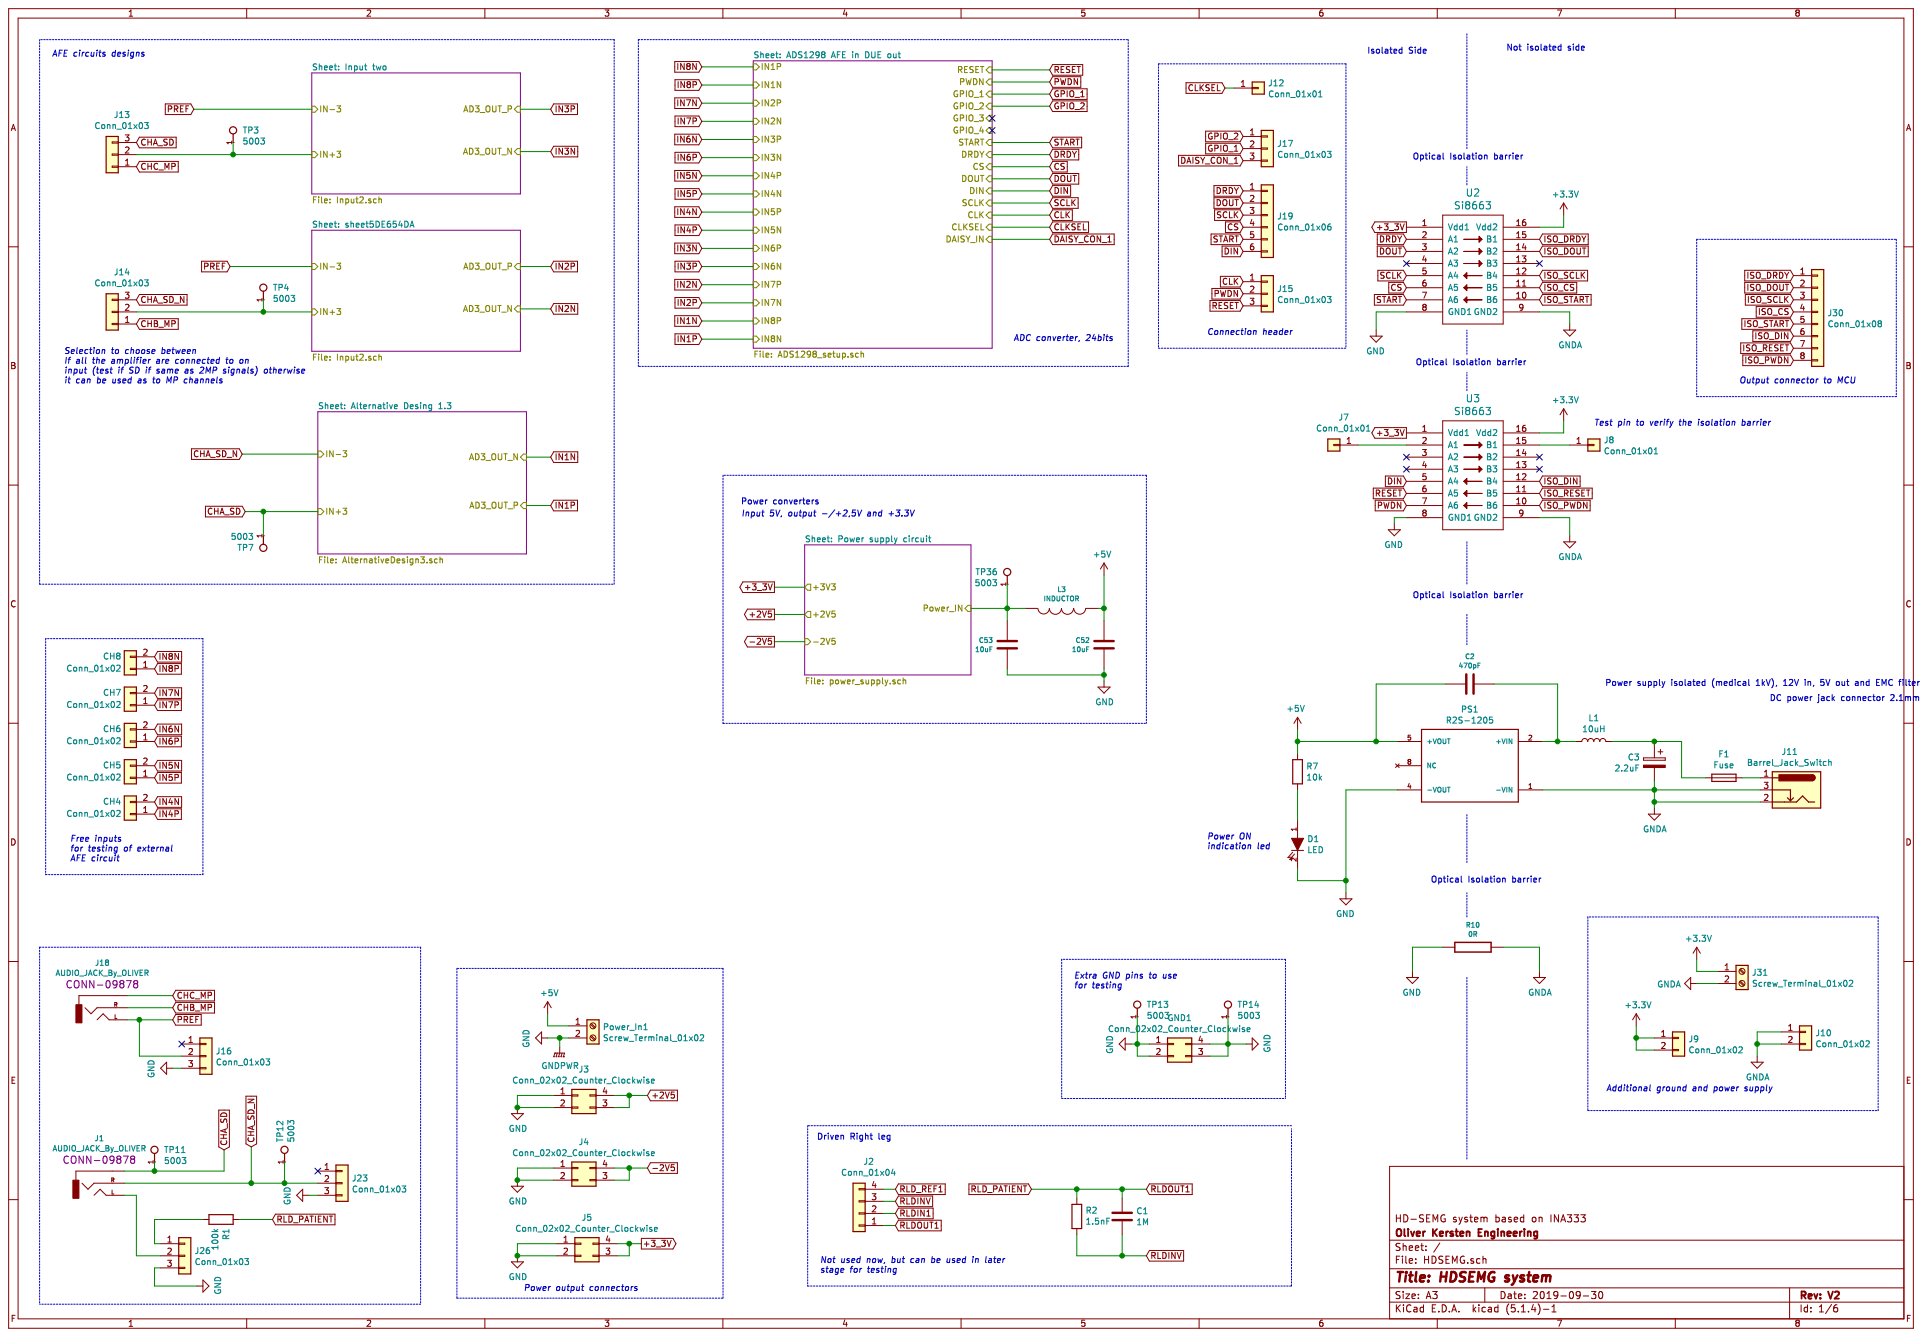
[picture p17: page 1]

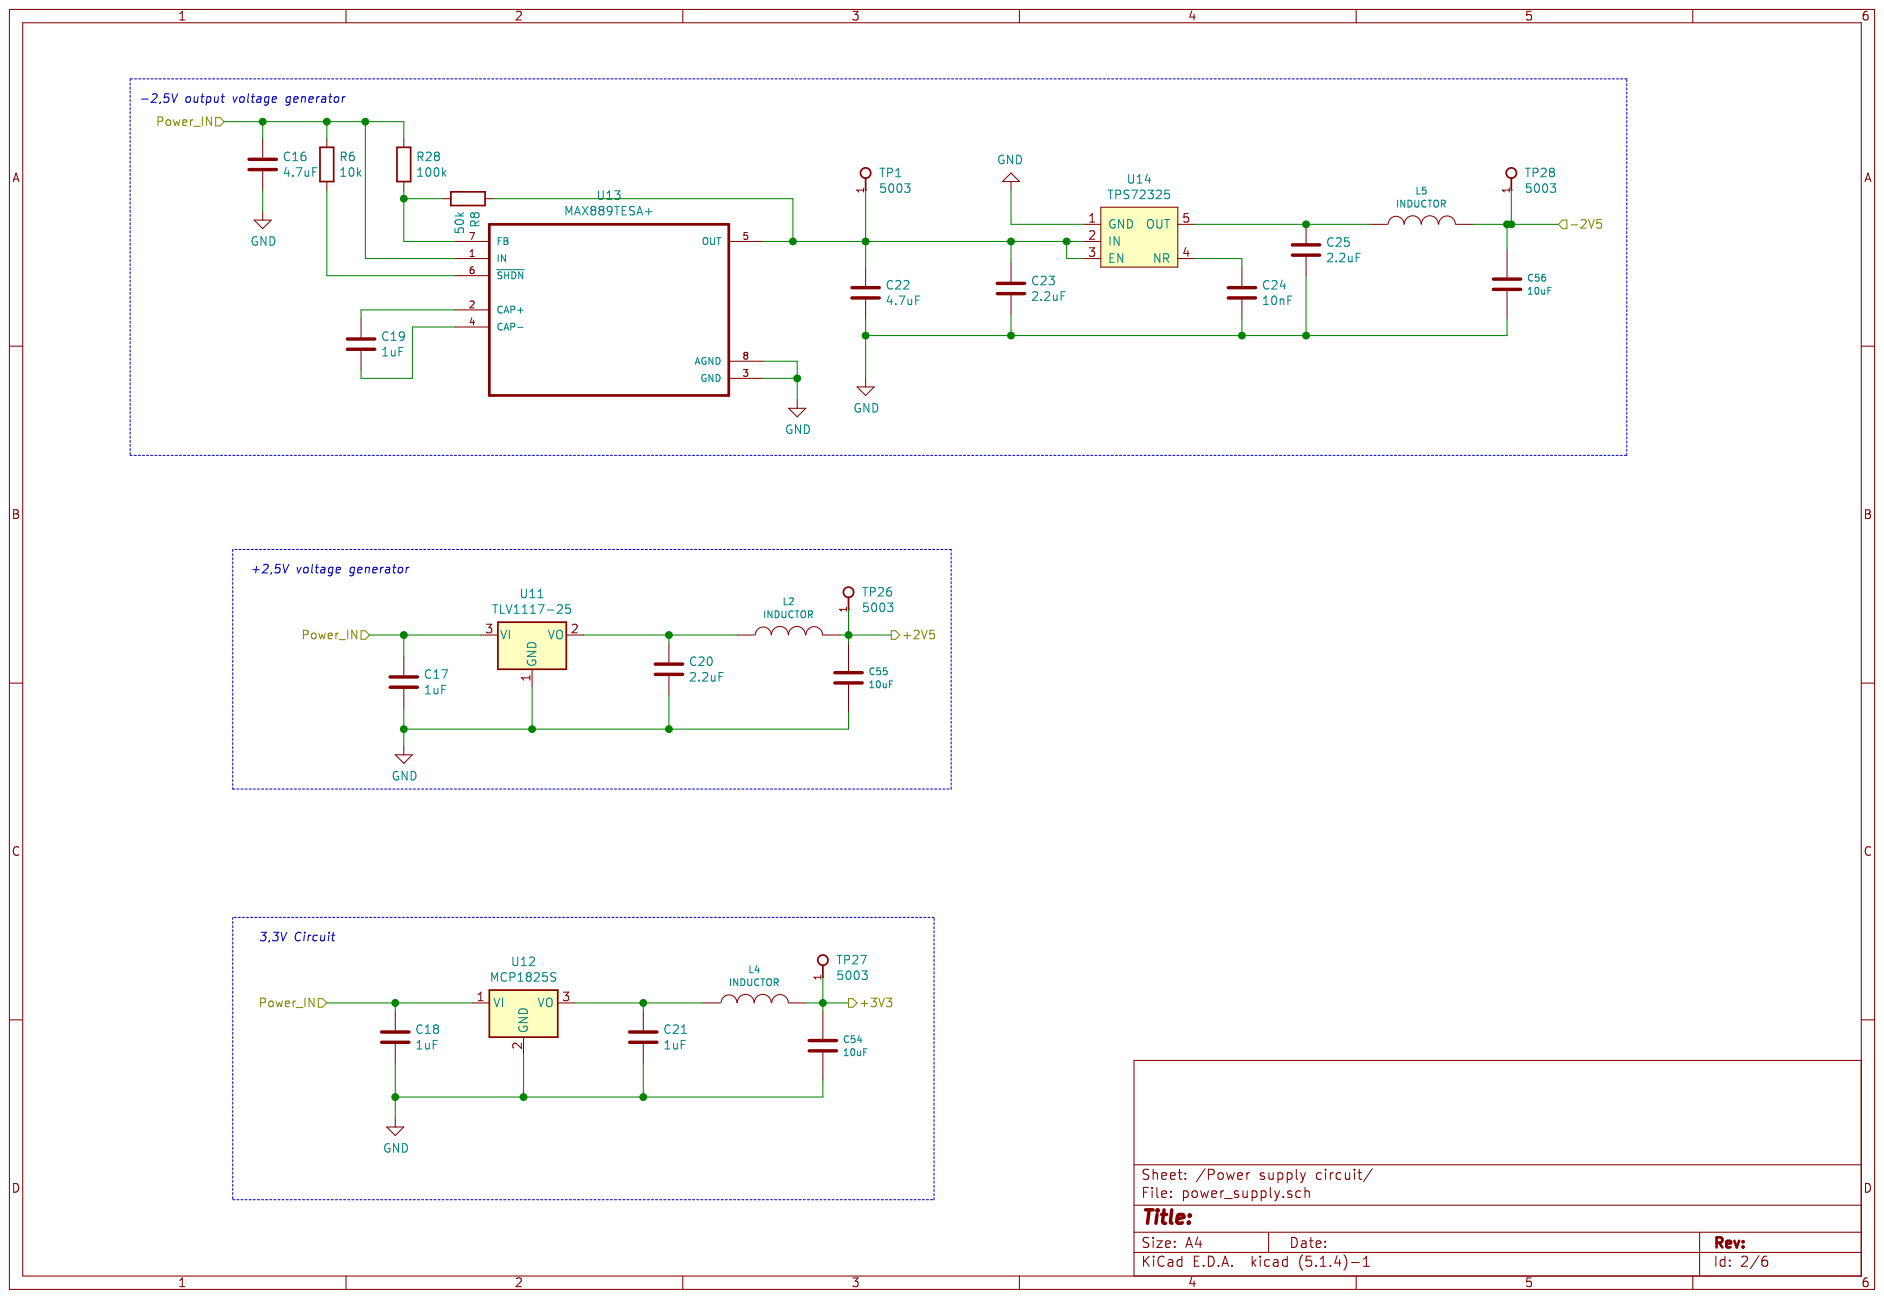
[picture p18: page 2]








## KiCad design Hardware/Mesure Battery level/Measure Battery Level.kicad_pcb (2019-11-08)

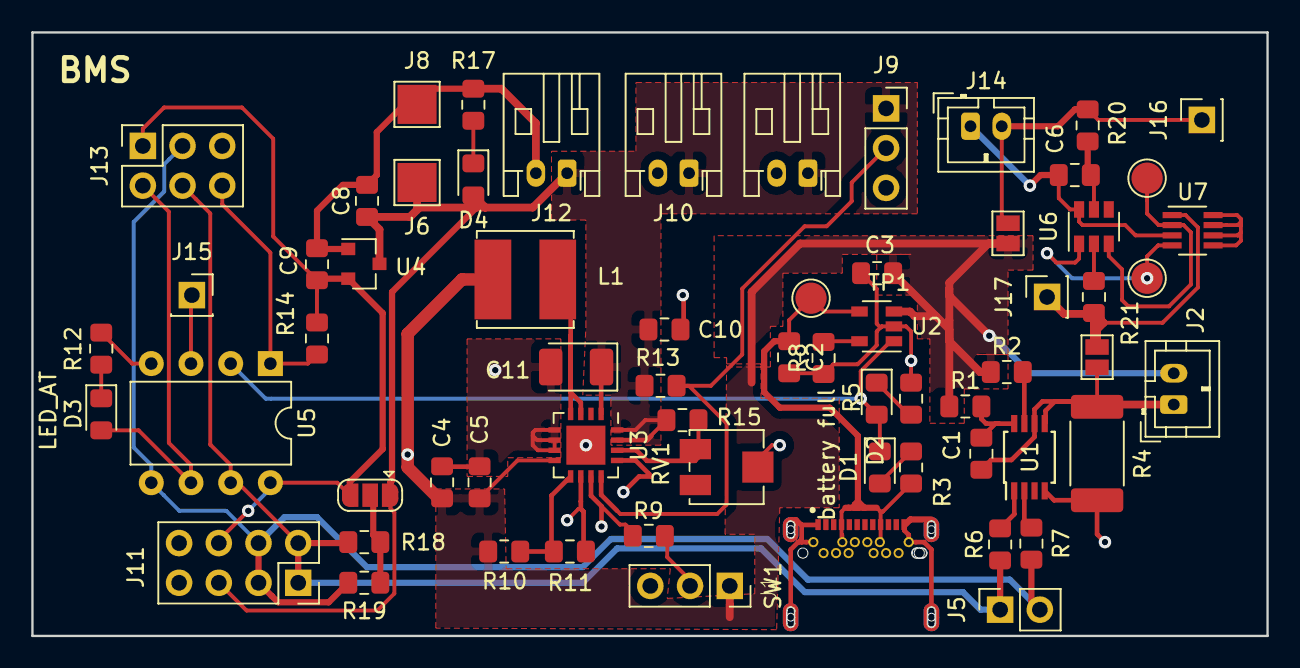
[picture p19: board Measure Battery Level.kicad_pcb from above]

Board: 2 copper layers, 79.0 x 38.6 mm, 65 parts (0 on the bottom side), 36 nets.

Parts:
C1: 100nF; C_0805_2012Metric_Pad1.15x1.40mm_HandSolder
C2, C3, C4: 10uF; C_0805_2012Metric_Pad1.15x1.40mm_HandSolder
C5: 0.1uF; C_0805_2012Metric_Pad1.15x1.40mm_HandSolder
C6: C; C_0805_2012Metric_Pad1.15x1.40mm_HandSolder
C8, C9: 1uF; C_0805_2012Metric_Pad1.15x1.40mm_HandSolder
C10: 2.2uF; C_0805_2012Metric_Pad1.15x1.40mm_HandSolder
C11: 100UF(tan); CP_EIA-3528-12_Kemet-T_Pad1.50x2.35mm_HandSolder
D1: bat charging; LED_0805_2012Metric_Pad1.15x1.40mm_HandSolder
D2: battery full; LED_0805_2012Metric_Pad1.15x1.40mm_HandSolder
D3: LED_AT; LED_0805_2012Metric_Pad1.15x1.40mm_HandSolder
D4: LED; LED_0805_2012Metric_Pad1.15x1.40mm_HandSolder
J1: USB4065-XX-X_REVA; GCT_USB4065-XX-X_REVA
J2, J14: CONN_02JST-PTH-2; JST_PH_B2B-PH-K_1x02_P2.00mm_Vertical
J5: Debug header; PinSocket_1x02_P2.54mm_Vertical
J6: 5V; TestPoint_Pad_2.5x2.5mm
J7, J10, J12: POWER_OUT; JST_PH_S2B-PH-K_1x02_P2.00mm_Horizontal
J8: GND; TestPoint_Pad_2.5x2.5mm
J9: Conn_01x03; PinSocket_1x03_P2.54mm_Vertical
J11: Conn_02x04_Odd_Even; PinSocket_2x04_P2.54mm_Vertical
J13: Conn_02x03_Odd_Even; PinSocket_2x03_P2.54mm_Vertical
J15, J16, J17: Conn_01x01; PinSocket_1x01_P2.54mm_Vertical
JP1: Jumper_3_Open; SolderJumper-3_P1.3mm_Open_RoundedPad1.0x1.5mm
JP2, JP3: Jumper; SolderJumper-2_P1.3mm_Open_Pad1.0x1.5mm
L1: 6.8uH; L_Bourns_SRN6045TA
R1: 500R; R_0805_2012Metric_Pad1.15x1.40mm_HandSolder
R2: 1000R; R_0805_2012Metric_Pad1.15x1.40mm_HandSolder
R3, R5, R12, R17: 1K; R_0805_2012Metric_Pad1.15x1.40mm_HandSolder
R4: Rsns; R_2512_6332Metric_Pad1.52x3.35mm_HandSolder
R6, R7: 150R; R_0805_2012Metric_Pad1.15x1.40mm_HandSolder
R8: Charge Current; R_0805_2012Metric_Pad1.15x1.40mm_HandSolder
R9, R20, R21: R; R_0805_2012Metric_Pad1.15x1.40mm_HandSolder
R10: 1.8MR; R_0805_2012Metric_Pad1.15x1.40mm_HandSolder
R11: 330k; R_0805_2012Metric_Pad1.15x1.40mm_HandSolder
R13: 2MOhm; R_0805_2012Metric_Pad1.15x1.40mm_HandSolder
R14: 10K; R_0805_2012Metric_Pad1.15x1.40mm_HandSolder
R15: 1.8Mohm; R_0805_2012Metric_Pad1.15x1.40mm_HandSolder
R18, R19: 4.7K; R_0805_2012Metric_Pad1.15x1.40mm_HandSolder
RV1: R_POT_TRIM; Potentiometer_Bourns_3314J_Vertical
SW1: Switch_SW_SPDT; PinSocket_1x03_P2.54mm_Vertical
TP1, TP2, TP3: TestPoint; TestPoint_Pad_D2.0mm
U1: ds2745_oliver; TSSOP-8_3x3mm_P0.65mm
U2: MCP73831; SOT-23-5
U3: TPS61090; QFN-16-1EP_4x4mm_P0.65mm_EP2.5x2.5mm
U4: MCP1703A-3302_SOT23; SOT-23
U5: ATtiny85-20PU; DIP-8_W7.62mm
U6: AP9101C; SOT-23-6
U7: ECH8693R; TSOT-23-8

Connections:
+3V3: C9.1, J11.6, J13.1, JP1.3, R14.1, U4.2, U5.8
+5V: C8.1, C10.1, C11.1, D4.2, J6.1, J7.1, J9.1, J10.1, J11.5, J12.1, JP1.1, R13.1, R15.1, U3.1, U3.15, U3.16, U4.3
+BATT: C3.1, C4.1, C5.1, J2.2, JP2.2, L1.1, R1.1, R2.1, R10.1, SW1.1, U2.3, U3.8
/ENABLE: R9.2, U3.11
/FB: R15.2, RV1.1, U3.14
/LBO: J9.2, R13.2, U3.12
/MISO: D3.2, J13.2, U5.6
/MOSI: J5.2, J11.3, J11.4, J13.3, R7.1, R19.1, U5.5
/RST: J13.6, R14.2, U5.1
/SCK: J5.1, J11.1, J11.2, J13.4, R6.1, R18.1, U5.7
/Status_Battery: D1.1, D2.2, U2.1, U5.2
GND: C2.2, C3.2, C4.2, C5.2, C8.2, C9.2, C10.2, C11.2, J1.1, J1.2, J1.3, J1.4, J1.A1, J1.A12, J1.B1, J1.B12, J7.2, J8.1, J9.3, J10.2, J11.7, J11.8, J12.2, J13.5, R4.1, R5.2, R8.1, R11.2, R12.1, R17.1, RV1.2, SW1.3, U1.4, U2.2, U3.5, U3.6, U3.7, U3.10, U3.13, U3.17, U4.1, U5.4
unnamed: C1.1, R1.2, U1.8
unnamed: C1.2, J2.1, JP3.2, R4.2, U1.5, U1.6
unnamed: C2.1, J1.A4, J1.A9, J1.B4, J1.B9, R3.2, TP1.1, U2.4
unnamed: C6.1, R20.1, U6.5
unnamed: C6.2, J14.1, U6.6, U7.3
unnamed: D1.2, R3.1
unnamed: D2.1, R5.1
unnamed: D3.1, R12.2
unnamed: D4.1, R17.2
unnamed: J14.2, J16.1, JP2.1, R20.2
unnamed: J15.1, U5.3
unnamed: J17.1, JP3.1, R21.1, U7.1
unnamed: JP1.2, R18.2, R19.2
unnamed: L1.2, U3.3, U3.4
unnamed: R2.2, U1.7
unnamed: R6.2, U1.1
unnamed: R7.2, U1.2
unnamed: R8.2, U2.5
unnamed: R9.1, SW1.2
unnamed: R10.2, R11.1, U3.9
unnamed: R21.2, U6.2
unnamed: TP2.1, U6.1, U7.4
unnamed: TP3.1, U6.3, U7.2
unnamed: U7.5, U7.6, U7.7, U7.8

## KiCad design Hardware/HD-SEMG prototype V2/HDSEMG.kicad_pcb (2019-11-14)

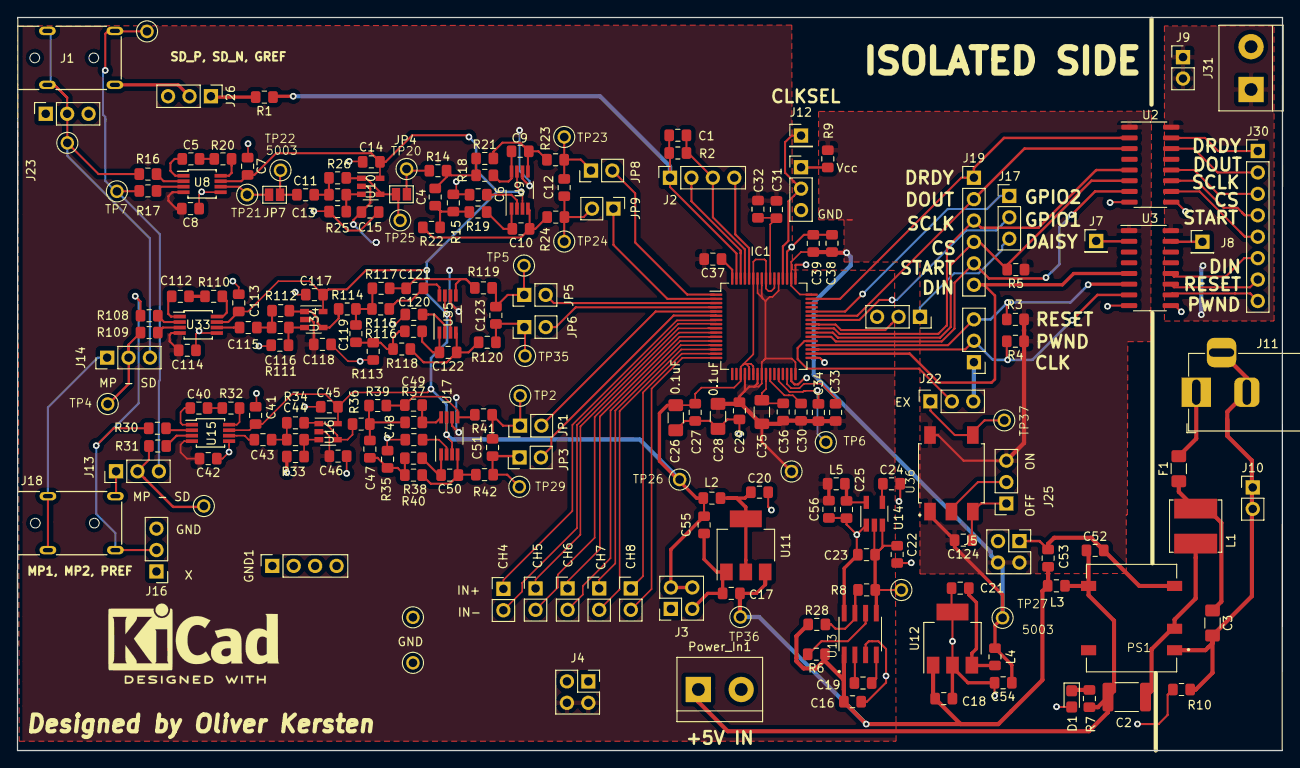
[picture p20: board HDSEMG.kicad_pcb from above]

Board: 2 copper layers, 150.0 x 86.9 mm, 209 parts (0 on the bottom side), 140 nets.

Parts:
C1: 1M; C_0805_2012Metric_Pad1.15x1.40mm_HandSolder
C2: 470pF; Fuse_1812_4532Metric_Pad1.30x3.40mm_HandSolder
C3: 2.2uF; C_1206_3216Metric_Pad1.42x1.75mm_HandSolder
C4: 47nF; C_0805_2012Metric_Pad1.15x1.40mm_HandSolder
C5, C16, C22, C40, C112: 4.7uF; C_0805_2012Metric_Pad1.15x1.40mm_HandSolder
C6, C48, C120: 220nF; C_0805_2012Metric_Pad1.15x1.40mm_HandSolder
C7, C8, C14, C15, C41, C42, C45, C46, C113, C114, C117, C118: 100n; C_0805_2012Metric_Pad1.15x1.40mm_HandSolder
C9, C10, C50, C122: 2.2nF; C_0805_2012Metric_Pad1.15x1.40mm_HandSolder
C11, C13, C43, C44, C115, C116: 100nF; C_0805_2012Metric_Pad1.15x1.40mm_HandSolder
C12, C51, C123: 33nF; C_0805_2012Metric_Pad1.15x1.40mm_HandSolder
C17, C18, C19, C21, C27, C29, C30, C31, C33, C39: 1uF; C_0805_2012Metric_Pad1.15x1.40mm_HandSolder
C20, C23, C25: 2.2uF; C_0805_2012Metric_Pad1.15x1.40mm_HandSolder
C24, C124: 10nF; C_0805_2012Metric_Pad1.15x1.40mm_HandSolder
C26, C28: 0.1uF; C_1206_3216Metric_Pad1.42x1.75mm_HandSolder
C32: .1uF; C_0805_2012Metric_Pad1.15x1.40mm_HandSolder
C34: 22uF; C_0805_2012Metric_Pad1.15x1.40mm_HandSolder
C35: 10uF; C_1206_3216Metric
C36: 0.1u; C_0805_2012Metric_Pad1.15x1.40mm_HandSolder
C37: 1nF; C_0805_2012Metric_Pad1.15x1.40mm_HandSolder
C38: 0.1uF; C_0805_2012Metric_Pad1.15x1.40mm_HandSolder
C47, C119: 47n; C_0805_2012Metric_Pad1.15x1.40mm_HandSolder
C49, C121: 2.2n; C_0805_2012Metric_Pad1.15x1.40mm_HandSolder
C52, C53, C54, C55, C56: 10uF; C_0805_2012Metric_Pad1.15x1.40mm_HandSolder
CH4, CH5, CH6, CH7, CH8: Conn_01x02; PinHeader_1x02_P2.54mm_Vertical
D1: LED; D_0805_2012Metric_Castellated
F1: Fuse; Fuse_1206_3216Metric_Pad1.42x1.75mm_HandSolder
GND1: Conn_02x02_Counter_Clockwise; PinSocket_1x04_P2.54mm_Vertical
IC1: ADS1298_By_Oliver; TQFP-64_10x10mm_P0.5mm
J1, J18: AUDIO_JACK_By_OLIVER; MX387GL
J2: Conn_01x04; PinSocket_1x04_P2.54mm_Vertical
J3, J4, J5: Conn_02x02_Counter_Clockwise; PinSocket_2x02_P2.54mm_Vertical
J7, J8, J12: Conn_01x01; PinHeader_1x01_P2.54mm_Vertical
J9, J10: Conn_01x02; PinHeader_1x02_P2.54mm_Vertical
J11: Barrel_Jack_Switch; BarrelJack_Horizontal
J13, J14, J15, J16, J17, J24, J26: Conn_01x03; PinHeader_1x03_P2.54mm_Vertical
J19: Conn_01x06; PinHeader_1x06_P2.54mm_Vertical
J21, J22, J23, J25: Conn_01x03; PinSocket_1x03_P2.54mm_Vertical
J30: Conn_01x08; PinHeader_1x08_P2.54mm_Vertical
J31: Screw_Terminal_01x02; TerminalBlock_bornier-2_P5.08mm
JP1, JP3, JP5, JP6, JP8, JP9: Jumper; PinHeader_1x02_P2.54mm_Vertical
JP4, JP7: Jumper; SolderJumper-2_P1.3mm_Open_Pad1.0x1.5mm
L1: 10uH; L_Bourns_SRN6045TA
L2, L3, L4, L5: INDUCTOR; L_0805_2012Metric_Pad1.15x1.40mm_HandSolder
PS1: R2S-1205; CONV_R2S-1205
Power_In1: Screw_Terminal_01x02; TerminalBlock_bornier-2_P5.08mm
R1, R28: 100k; R_0805_2012Metric_Pad1.15x1.40mm_HandSolder
R2: 1.5nF; R_0805_2012Metric_Pad1.15x1.40mm_HandSolder
R3, R4, R5: 10K; R_0805_2012Metric_Pad1.15x1.40mm_HandSolder
R6, R7, R9: 10k; R_0805_2012Metric_Pad1.15x1.40mm_HandSolder
R8: 50k; R_0805_2012Metric_Pad1.15x1.40mm_HandSolder
R10: 0R; R_0805_2012Metric_Pad1.15x1.40mm_HandSolder
R14, R15, R35, R36, R113, R114: 1.1k; R_0805_2012Metric_Pad1.15x1.40mm_HandSolder
R16, R17, R30, R31, R108, R109: 51k; R_0805_2012Metric_Pad1.15x1.40mm_HandSolder
R18, R19, R37, R38, R115, R116: 5.6k; R_0805_2012Metric_Pad1.15x1.40mm_HandSolder
R20, R32, R110: 4300R; R_0805_2012Metric_Pad1.15x1.40mm_HandSolder
R21, R22, R39, R40, R117, R118: 11k; R_0805_2012Metric_Pad1.15x1.40mm_HandSolder
R23, R24, R41, R42, R119, R120: 50R; R_0805_2012Metric_Pad1.15x1.40mm_HandSolder
R25, R34, R112: 220k; R_0805_2012Metric_Pad1.15x1.40mm_HandSolder
R26: 110k; R_0805_2012Metric_Pad1.15x1.40mm_HandSolder
R33, R111: 430k; R_0805_2012Metric_Pad1.15x1.40mm_HandSolder
TP1, TP3, TP4, TP6, TP7, TP11, TP12, TP13, TP14, TP20, TP21, TP22, TP23, TP24, TP25, TP26, TP27, TP28, TP29, TP35, TP36, TP37: 5003; keystone_PCB_TEST_PIN
TP2, TP5: 5003; TPCW51D250H460P
U2, U3: Si8663; SOIC-16_3.9x9.9mm_P1.27mm
U8, U15, U33: INA333AIDGKR; MSOP-8_3x3mm_P0.65mm
U9, U17, U35: THS4521IDGKT; VSSOP-8_3.0x3.0mm_P0.65mm
U10, U16, U34: OPA333xxDBV; SOT-23-5
U11: TLV1117-25; SOT-223-3_TabPin2
U12: MCP1825S; SOT-223-3_TabPin2
U13: MAX889TESA+; SOIC127P600X175-8N
U14: TPS72325; SOT-23-5_HandSoldering
U36: 357LB3CI002M0480; SOIC254P1016X460-5N

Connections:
+2V5: C7.2, C14.1, C26.1, C27.1, C41.2, C45.1, C55.1, C113.2, C117.1, IC1.19, IC1.21, IC1.22, IC1.54, IC1.56, IC1.59, J3.3, J3.4, L2.2, TP26.1, U8.7, U9.3, U9.7, U10.5, U15.7, U16.5, U17.3, U17.7, U33.7, U34.5, U35.3, U35.7
+3V3: J9.1, J9.2, J31.1, U2.16, U3.16
+3_3V: C38.1, C39.1, C54.1, C124.2, IC1.48, IC1.50, J5.3, J5.4, J25.3, L4.2, R3.1, R4.1, R5.1, R9.1, TP27.1, U2.1, U3.1, U36.1, U36.6
+5V: C2.1, C52.1, L3.2, PS1.5, Power_In1.1, R7.1
-2V5: C8.2, C15.1, C28.1, C29.1, C30.2, C31.2, C32.2, C33.2, C34.2, C35.2, C36.2, C37.2, C42.2, C46.1, C56.1, C114.2, C118.1, IC1.20, IC1.23, IC1.24, IC1.32, IC1.53, IC1.57, IC1.58, J4.3, J4.4, L5.2, TP28.1, U8.4, U9.6, U10.2, U15.4, U16.2, U17.6, U33.4, U34.2, U35.6
/ADS1298 AFE in DUE out/EX_CLK_SIG: J22.1, TP37.1, U36.4
/Alternative Desing 1.3/low_pass_out: JP4.1, R26.1, TP25.1, U10.1, U10.4
/Input two/IN+3: J13.2, R31.2, TP3.1
/Power supply circuit/Power_IN: C16.1, C17.1, C18.1, C53.1, L3.1, R6.1, R28.1, TP36.1, U11.3, U12.1, U13.1
/sheet5DE654DA/IN+3: J14.2, R109.2, TP4.1
CHA_SD: J1.3, J13.3, R17.2, TP7.1, TP11.1
CHA_SD_N: J1.2, J14.3, J23.2, R16.2, TP12.1
CHB_MP: J14.1, J18.2
CHC_MP: J13.1, J18.3
CLK: J15.1, J22.3
CLKSEL: IC1.52, J12.1, J24.2
CS: IC1.39, J19.4, R5.2, U2.6
DAISY_CON_1: J17.3, J21.1
DGND: C6.2, C7.1, C8.1, C14.2, C15.2, C16.2, C17.2, C18.2, C20.2, C21.2, C22.2, C23.2, C24.2, C25.2, C26.2, C27.2, C28.2, C29.2, C38.2, C39.2, C41.1, C42.1, C45.2, C46.2, C48.2, C52.2, C53.2, C54.2, C55.2, C56.2, C113.1, C114.1, C117.2, C118.2, C120.2, C124.1, D1.2, GND1.1, GND1.2, GND1.3, GND1.4, IC1.31, IC1.33, IC1.49, IC1.51, J3.1, J3.2, J4.1, J4.2, J5.1, J5.2, J16.3, J21.3, J23.3, J24.3, J25.1, J26.3, PS1.4, Power_In1.2, R10.2, R15.1, R25.1, R33.1, R35.1, R111.1, R113.1, TP13.1, TP14.1, U2.8, U3.8, U8.5, U11.1, U12.2, U13.3, U13.8, U14.1, U15.5, U33.5, U36.3
DIN: IC1.34, J19.6, U3.5
DOUT: IC1.43, J19.2, U2.3
DRDY: IC1.47, J19.1, U2.2
GNDA: C3.2, J10.1, J10.2, J11.2, J11.3, J31.2, PS1.1, R10.1, U2.9, U3.9
GPIO_1: IC1.42, J17.2
GPIO_2: IC1.44, J17.1
IN1N: IC1.2, JP9.1
IN1P: IC1.1, JP8.2
IN2N: IC1.4, JP6.2
IN2P: IC1.3, JP5.2
IN3N: IC1.6, JP3.2
IN3P: IC1.5, JP1.2
IN4N: CH4.2, IC1.8
IN4P: CH4.1, IC1.7
IN5N: CH5.2, IC1.10
IN5P: CH5.1, IC1.9
IN6N: CH6.2, IC1.12
IN6P: CH6.1, IC1.11
IN7N: CH7.2, IC1.14
IN7P: CH7.1, IC1.13
IN8N: CH8.2, IC1.16
IN8P: CH8.1, IC1.15
ISO_CS: J30.4, U2.11
ISO_DIN: J30.6, U3.12
ISO_DOUT: J30.2, U2.14
ISO_DRDY: J30.1, U2.15
ISO_PWDN: J30.8, U3.10
ISO_RESET: J30.7, U3.11
ISO_SCLK: J30.3, U2.12
ISO_START: J30.5, U2.10
unnamed: C2.2, L1.2, PS1.2
unnamed: C3.1, F1.1, L1.1
unnamed: C4.1, R15.2, R19.1, R22.1
unnamed: C4.2, R14.2, R18.1, R21.1
unnamed: C5.1, U8.1
unnamed: C5.2, R20.2
unnamed: C6.1, U9.2
unnamed: C9.1, R21.2, R23.2, U9.5
unnamed: C9.2, R18.2, U9.8
unnamed: C10.1, R22.2, R24.1, U9.4
unnamed: C10.2, R19.2, U9.1
unnamed: C11.1, JP7.2, TP22.1
unnamed: C11.2, C13.1, R26.2
unnamed: C12.1, JP8.1, R23.1, TP23.1
unnamed: C12.2, JP9.2, R24.2, TP24.1
unnamed: C13.2, R25.2, U10.3
unnamed: C19.1, U13.2
unnamed: C19.2, U13.4
unnamed: C20.1, L2.1, U11.2
unnamed: C21.1, L4.1, U12.3
unnamed: C22.1, C23.1, R8.1, TP1.1, U13.5, U14.2, U14.3
unnamed: C24.1, U14.4
unnamed: C25.1, L5.1, U14.5
unnamed: C40.1, U15.1
unnamed: C40.2, R32.2
unnamed: C43.1, U15.6
unnamed: C43.2, C44.1, R34.2
unnamed: C44.2, R33.2, U16.3
unnamed: C47.1, R35.2, R38.1, R40.1
unnamed: C47.2, R36.2, R37.1, R39.1
unnamed: C48.1, U17.2
unnamed: C49.1, R39.2, R41.2, U17.5
unnamed: C49.2, R37.2, U17.8
unnamed: C50.1, R40.2, R42.1, U17.4
unnamed: C50.2, R38.2, U17.1
unnamed: C51.1, JP1.1, R41.1, TP2.1
unnamed: C51.2, JP3.1, R42.2, TP29.1
unnamed: C112.1, U33.1
unnamed: C112.2, R110.2
unnamed: C115.1, U33.6
unnamed: C115.2, C116.1, R112.2
unnamed: C116.2, R111.2, U34.3
unnamed: C119.1, R113.2, R116.1, R118.1
unnamed: C119.2, R114.2, R115.1, R117.1
unnamed: C120.1, U35.2
unnamed: C121.1, R117.2, R119.2, U35.5
unnamed: C121.2, R115.2, U35.8
unnamed: C122.1, R118.2, R120.1, U35.4
unnamed: C122.2, R116.2, U35.1
unnamed: C123.1, JP5.1, R119.1, TP5.1
unnamed: C123.2, JP6.1, R120.2, TP35.1
unnamed: D1.1, R7.2
unnamed: F1.2, J11.1
unnamed: IC1.37, J22.2
unnamed: IC1.41, J21.2
unnamed: J1.1, J26.2
unnamed: J7.1, U3.2
unnamed: J8.1, U3.15
unnamed: J24.1, R9.2
unnamed: J25.2, U36.2
unnamed: J26.1, R1.2
unnamed: JP4.2, R14.1, TP20.1
unnamed: JP7.1, TP21.1, U8.6
unnamed: R6.2, U13.6
unnamed: R16.1, U8.2
unnamed: R17.1, U8.3
unnamed: R20.1, U8.8
unnamed: R8.2, R28.2, U13.7
unnamed: R30.1, U15.2
unnamed: R31.1, U15.3
unnamed: R32.1, U15.8
unnamed: R34.1, R36.1, U16.1, U16.4
unnamed: R108.1, U33.2
unnamed: R109.1, U33.3
unnamed: R110.1, U33.8
unnamed: R112.1, R114.1, U34.1, U34.4
PREF: J16.2, J18.1, R30.2, R108.2
PWDN: IC1.35, J15.2, R4.2, U3.7
RESET: IC1.36, J15.3, R3.2, U3.6
RLDIN1: IC1.62, J2.2
RLDINV: C1.2, IC1.61, J2.3, R2.1
RLDOUT1: C1.1, IC1.63, J2.1, R1.1, R2.2
RLD_REF1: IC1.60, J2.4
SCLK: IC1.40, J19.3, U2.5
START: IC1.38, J19.5, U2.7
VCAP1_1: C34.1, IC1.28, TP6.1
VCAP2_1: C33.1, IC1.30
VCAP3_1: C31.1, C32.1, IC1.55
VCAP4_1: C30.1, IC1.26
VREFP1: C35.1, C36.1, IC1.25
WTC_1: C37.1, IC1.64

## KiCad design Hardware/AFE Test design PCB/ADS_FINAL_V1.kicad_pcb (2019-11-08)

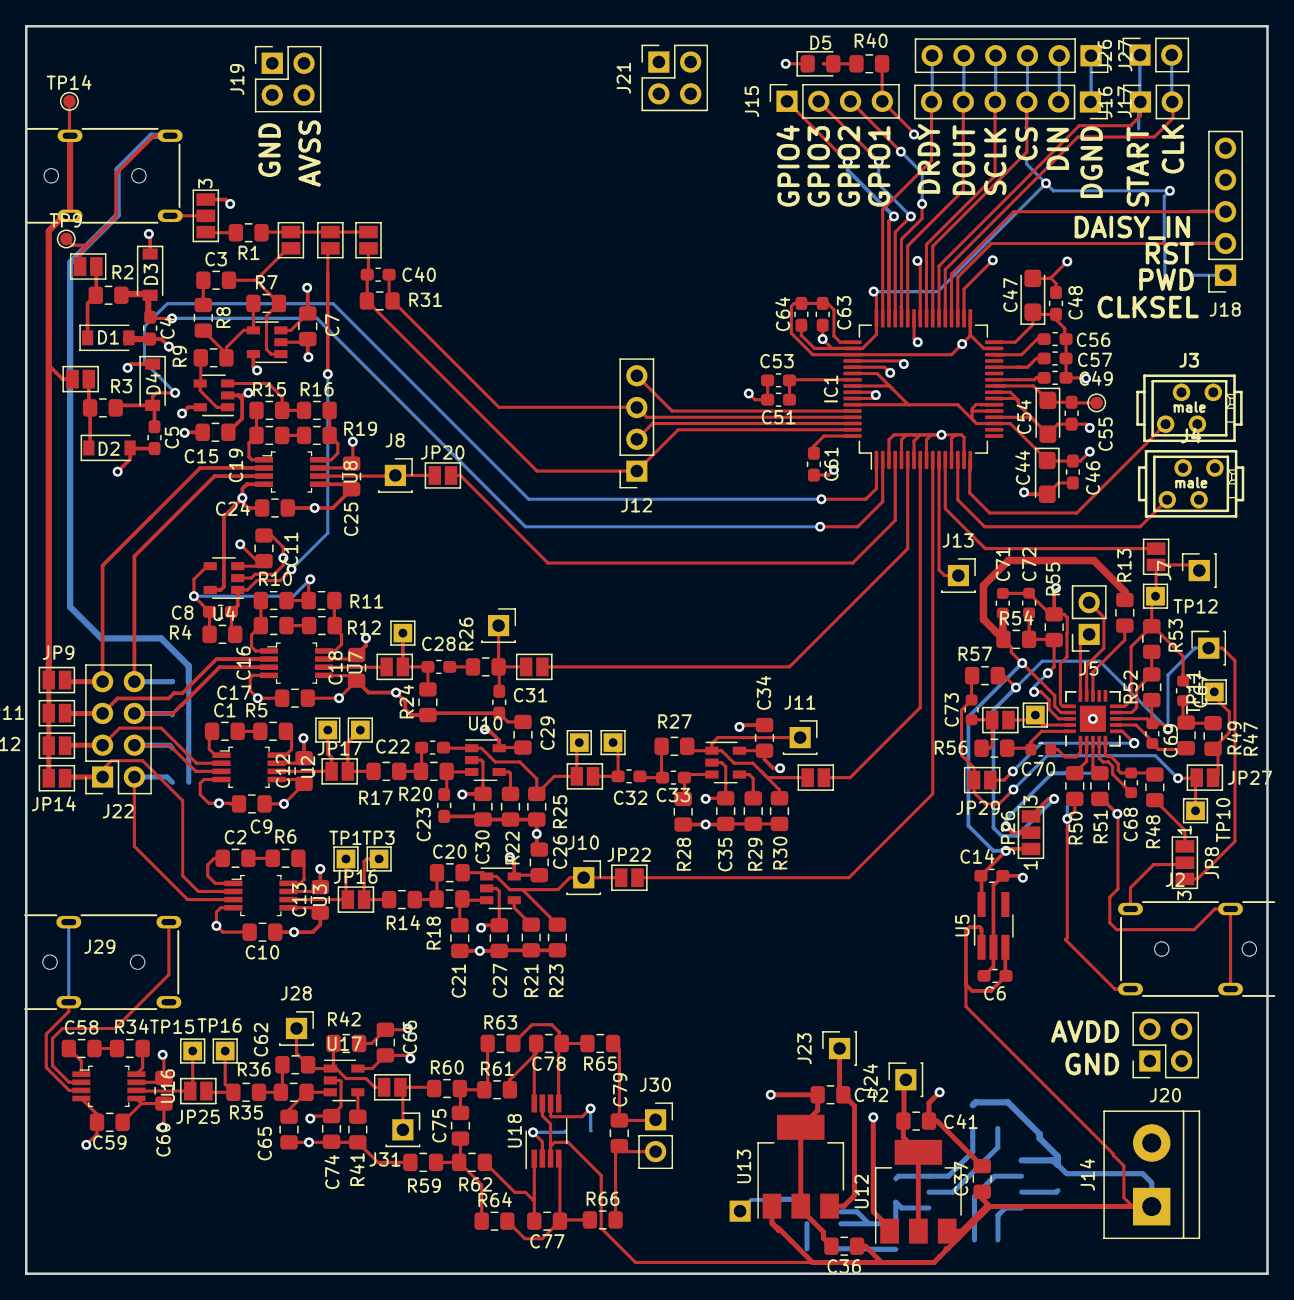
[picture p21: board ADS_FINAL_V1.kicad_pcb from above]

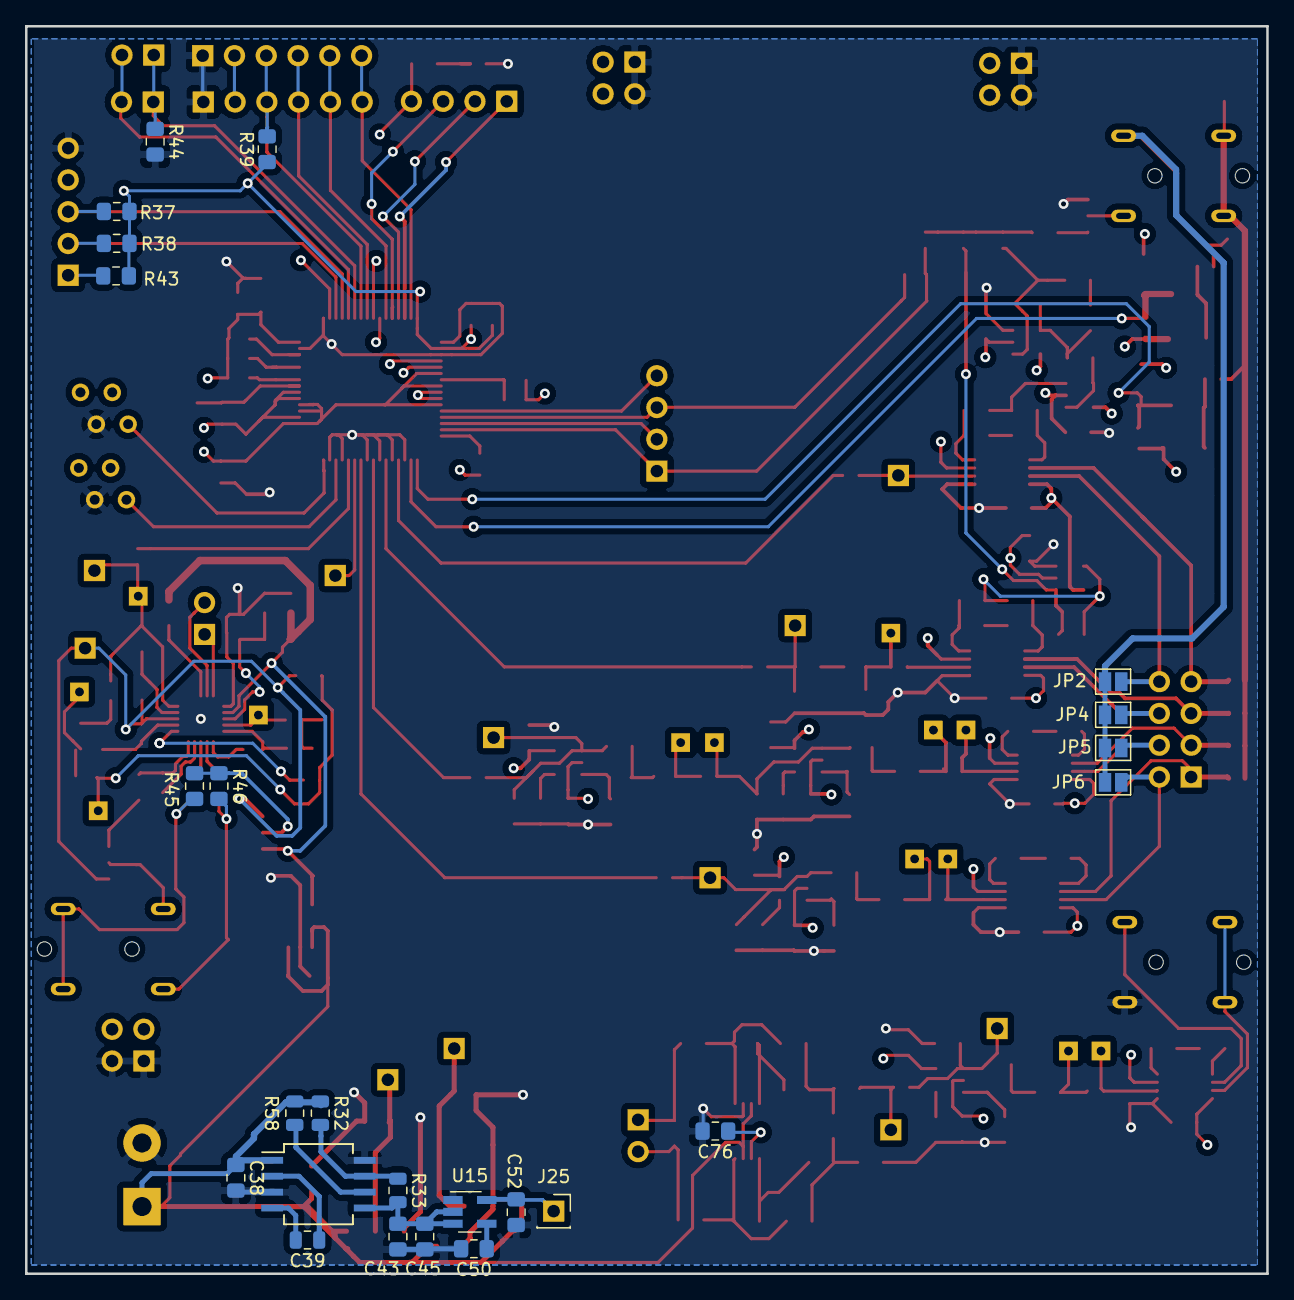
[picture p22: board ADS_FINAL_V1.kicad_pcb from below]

Board: 4 copper layers, 99.2 x 99.7 mm, 247 parts (24 on the bottom side), 150 nets.

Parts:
C1, C2, C16, C19, C58: 15u; C_0805_2012Metric_Pad1.15x1.40mm_HandSolder
C3: 1nF; C_0805_2012Metric_Pad1.15x1.40mm_HandSolder
C4, C5: 10pF; C_0603_1608Metric_Pad1.05x0.95mm_HandSolder
C6, C14, C49, C51, C56, C64: 1uF; C_0603_1608Metric_Pad1.05x0.95mm_HandSolder
C7, C9, C10, C11, C12, C13, C15, C17, C18, C24, C25, C26, C27, C29, C30, C34, C35, C59, C60, C66, C74, C75, C76, C77, C78, C79: 100n; C_0805_2012Metric_Pad1.15x1.40mm_HandSolder
C8: 1.5nF; C_0603_1608Metric_Pad1.05x0.95mm_HandSolder
C20, C21, C62, C65: 4.7nF; C_0805_2012Metric_Pad1.15x1.40mm_HandSolder
C22, C23: 4.7nF; C_0603_1608Metric_Pad1.05x0.95mm_HandSolder
C28, C31: 100n; C_0603_1608Metric_Pad1.05x0.95mm_HandSolder
C32, C33: 10nF; C_0603_1608Metric_Pad1.05x0.95mm_HandSolder
C36, C37, C41, C42: 1uF; C_0805_2012Metric_Pad1.15x1.40mm_HandSolder
C38, C43: 4.7uF; C_0805_2012Metric_Pad1.15x1.40mm_HandSolder
C39: 1uF; C_0805_2012Metric
C40: 1M; C_0603_1608Metric_Pad1.05x0.95mm_HandSolder
C44: 10uF; CP_EIA-3216-12_Kemet-S
C45, C52: 2.2uF; C_0805_2012Metric_Pad1.15x1.40mm_HandSolder
C46, C48, C55: 0.1u; C_0603_1608Metric_Pad1.05x0.95mm_HandSolder
C47, C54: 10uF; CP_EIA-3216-10_Kemet-I
C50: 10nF; C_0805_2012Metric_Pad1.15x1.40mm_HandSolder
C53: .1uF; C_0603_1608Metric_Pad1.05x0.95mm_HandSolder
C57: 22uF; C_0603_1608Metric_Pad1.05x0.95mm_HandSolder
C61: 1nF; C_0603_1608Metric_Pad1.05x0.95mm_HandSolder
C63: 0.1uF; C_0603_1608Metric_Pad1.05x0.95mm_HandSolder
C67, C68, C69: 1nF; C_0603_1608Metric
C70, C73: 1000nF; C_0603_1608Metric
C71, C72: 100nF; C_0603_1608Metric
D1, D2, D3, D4: D_Schottky; D_SOD-123
D5: LED; LED_0805_2012Metric_Pad1.15x1.40mm_HandSolder
IC1: ADS1298_By_Oliver; TQFP-64_10x10mm_P0.5mm
J1, J2, J29: AUDIO_JACK_By_OLIVER; MX387GL
J3, J4: external header 2; 0-215464-4_TH_4-pin_male
J5, J16, J26, J30: Conn_01x02; PinSocket_1x02_P2.54mm_Vertical
J6, J7, J8, J9, J10, J11, J13, J23, J24, J25, J28, J31: Conn_01x01; PinSocket_1x01_P2.54mm_Vertical
J12, J15: Conn_01x04; PinSocket_1x04_P2.54mm_Vertical
J14: Screw_Terminal_01x02; TerminalBlock_bornier-2_P5.08mm
J17, J27: DATA_OUT; PinSocket_1x06_P2.54mm_Vertical
J18: Conn_01x05; PinSocket_1x05_P2.54mm_Vertical
J19, J20, J21: Conn_02x02_Counter_Clockwise; PinSocket_2x02_P2.54mm_Vertical
J22: Conn_02x04_Counter_Clockwise; PinSocket_2x04_P2.54mm_Vertical
JP1, JP2, JP4, JP5, JP6, JP7, JP9, JP10, JP11, JP12, JP13, JP14, JP15, JP19: SolderJumper_2_Open; SolderJumper-2_P1.3mm_Open_Pad1.0x1.5mm
JP3, JP8: Jumper_3_Open; SolderJumper-3_P1.3mm_Open_Pad1.0x1.5mm_NumberLabels
JP16, JP17, JP18, JP20, JP21, JP22, JP23, JP24, JP25, JP30: Jumper; SolderJumper-2_P1.3mm_Open_Pad1.0x1.5mm
JP26: SolderJumper_3_Open; SolderJumper-3_P1.3mm_Open_Pad1.0x1.5mm_NumberLabels
JP27, JP28, JP29: Jumper_2_Open; SolderJumper-2_P1.3mm_Open_Pad1.0x1.5mm
M1: AD8232; LFCSP-20-1EP_4x4mm_P0.5mm_EP2.1x2.1mm
R1, R7: 100k; R_0805_2012Metric_Pad1.15x1.40mm_HandSolder
R2, R3: 5k; R_0805_2012Metric_Pad1.15x1.40mm_HandSolder
R4: 1M; R_0805_2012Metric_Pad1.15x1.40mm_HandSolder
R5, R6, R10, R11, R12, R15, R16, R19, R21, R22, R24, R26, R29, R34, R41: 1K; R_0805_2012Metric_Pad1.15x1.40mm_HandSolder
R8, R13, R37, R43, R44: 10k; R_0805_2012Metric_Pad1.15x1.40mm_HandSolder
R9, R38: 10K; R_0805_2012Metric_Pad1.15x1.40mm_HandSolder
R14, R17, R35: 36k; R_0805_2012Metric_Pad1.15x1.40mm_HandSolder
R18, R20, R36, R56, R57, R59, R60, R61, R62, R63, R64, R65, R66: 130k; R_0805_2012Metric_Pad1.15x1.40mm_HandSolder
R23, R42: 9k; R_0805_2012Metric_Pad1.15x1.40mm_HandSolder
R25: 30k; R_0805_2012Metric_Pad1.15x1.40mm_HandSolder
R27: 1.1M; R_0805_2012Metric_Pad1.15x1.40mm_HandSolder
R28: 2.2M; R_0805_2012Metric_Pad1.15x1.40mm_HandSolder
R30: 3K; R_0805_2012Metric_Pad1.15x1.40mm_HandSolder
R31: 1.5nF; R_0805_2012Metric_Pad1.15x1.40mm_HandSolder
R32: 100k; R_0805_2012Metric
R33: 50k; R_0805_2012Metric
R39: 100K; R_0805_2012Metric_Pad1.15x1.40mm_HandSolder
R40, R47, R49, R52, R53: R; R_0805_2012Metric_Pad1.15x1.40mm_HandSolder
R45, R46, R54, R55: 10M; R_0805_2012Metric_Pad1.15x1.40mm_HandSolder
R48: 390k; R_0805_2012Metric_Pad1.15x1.40mm_HandSolder
R50, R51: 180k; R_0805_2012Metric_Pad1.15x1.40mm_HandSolder
R58: 10k; R_0805_2012Metric
TP1, TP2, TP3, TP4, TP5, TP6, TP7, TP10, TP11, TP12, TP13, TP15, TP16: TestPoint; TestPoint_THTPad_1.5x1.5mm_Drill0.7mm
TP8, TP9, TP14: TestPoint; TestPoint_Pad_D1.0mm
U1, U4, U6, U9, U10, U11, U17: OPA333xxDBV; SOT-23-5
U2, U3, U7, U8, U16: INA333AIDGKR; TSSOP-8_W3mm
U5: ADP150; TSOT-23-5_HandSoldering
U12: TLV1117-25; SOT-223-3_TabPin2
U13: MCP1825S; SOT-223-3_TabPin2
U14: MAX889T; SO-8_5.3x6.2mm_P1.27mm
U15: TPS72325; SOT-23-5_HandSoldering
U18: THS4521IDGKT; VSSOP-8_3.0x3.0mm_P0.65mm

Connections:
+5V: C6.1, C36.1, C37.1, C38.1, J14.1, R32.1, R58.1, U5.1, U5.3, U12.3, U13.1, U14.1, U18.3, U18.7
/sheet794AF31F/3V_IN: C14.1, C71.2, JP26.1, M1.17, R13.2, R54.1, U5.5
/sheet794AF31F/EMG_OUT: C67.1, J7.1, JP19.1, M1.10, R53.2, TP12.1
/sheet794AF31F/SDN_MCU: M1.13, R13.1
AD-DC1: J5.2, M1.14
AVDD: C7.1, C11.1, C12.2, C13.2, C15.1, C18.2, C25.2, C26.1, C29.1, C34.1, C41.1, C44.1, C46.1, C60.2, C66.1, D3.1, D4.1, IC1.19, IC1.21, IC1.22, IC1.54, IC1.56, IC1.59, J3.1, J4.1, J20.3, J20.4, J24.1, U1.2, U2.7, U3.7, U4.2, U6.2, U7.7, U8.7, U9.5, U10.5, U11.5, U12.2, U16.7, U17.5
AVSS: C4.2, C5.2, C9.2, C10.2, C17.2, C24.2, C27.1, C30.1, C35.1, C47.1, C48.1, C49.2, C51.2, C52.1, C53.2, C54.2, C55.2, C56.2, C57.2, C59.2, C61.2, C74.1, D1.2, D2.2, IC1.20, IC1.23, IC1.24, IC1.32, IC1.53, IC1.57, IC1.58, J3.3, J4.3, J19.3, J19.4, J25.1, U1.5, U2.4, U3.4, U4.5, U6.5, U7.4, U8.4, U9.2, U10.2, U11.2, U15.5, U16.4, U17.2
CLK: IC1.37, J16.2, J26.2
CLKSEL: IC1.52, J18.1, R43.2
CS: IC1.39, J17.3, J27.3, R39.2
DAISY_CON_1: IC1.41, J18.4
DGND: C6.2, C7.2, C9.1, C10.1, C11.2, C12.1, C13.1, C14.2, C15.2, C17.1, C18.1, C21.1, C23.1, C24.1, C25.1, C26.2, C27.2, C29.2, C30.2, C31.1, C34.2, C35.2, C36.2, C37.2, C38.2, C41.2, C42.2, C43.2, C44.2, C45.2, C46.2, C47.2, C48.2, C50.2, C52.2, C59.1, C60.1, C63.2, C64.2, C65.1, C66.2, C71.1, C72.2, C74.2, C76.2, D5.1, IC1.3, IC1.5, IC1.7, IC1.9, IC1.13, IC1.15, IC1.31, IC1.33, IC1.49, IC1.51, J3.2, J4.2, J14.2, J17.1, J18.5, J19.1, J19.2, J20.1, J20.2, J21.1, J21.2, J27.1, J29.1, JP3.3, M1.16, M1.21, R21.1, R22.1, R23.1, R24.1, R25.1, R28.1, R29.1, R30.1, R41.1, R42.1, R44.2, R55.1, R59.1, U1.3, U2.5, U3.5, U4.3, U5.2, U7.5, U8.5, U12.1, U13.2, U14.3, U14.8, U15.1, U16.5, U18.6
DIN: IC1.34, J17.2, J27.2
DOUT: IC1.43, J17.5, J27.5
DRDY: IC1.47, J17.6, J27.6
DRL3: JP8.1, R48.2
DVDD: C42.1, C63.1, C64.1, IC1.48, IC1.50, J21.3, J21.4, J23.1, R37.1, R38.1, R39.1, R43.1, U13.3
FR1: J5.1, M1.15
GPIO_1: IC1.42, J15.4, R40.1
GPIO_2: IC1.44, J15.3
GPIO_3: IC1.45, J15.2
GPIO_4: IC1.46, J15.1
IN1N: C5.1, D4.2, IC1.1, R3.1
IN1NI: D2.1, JP7.2, R3.2
IN1P: C4.1, D3.2, IC1.2, R2.1
IN1PI: D1.1, JP1.2, R2.2
IN2: IC1.4, JP20.2
IN3: IC1.6, JP21.2
IN4: IC1.8, JP24.2
IN5: IC1.10, JP22.2
IN6: IC1.14, J4.4
IN7: IC1.16, J3.4
IN8: IC1.12, JP19.2
IN+2: J22.8, JP2.2, U8.3
IN+3: J22.6, JP4.2, U7.3
IN+4: J22.4, JP5.2, U2.3
IN+5: J22.2, JP6.2, U3.3
IN+8: J2.2, R45.2, R51.2
IN+9: J29.2, U16.3
IN-2: J22.7, JP9.2, U8.2
IN-3: J22.5, JP11.2, U7.2
IN-4: J22.3, JP12.2, U2.2
IN-5: J22.1, JP14.2, U3.2
IN-8: J2.3, R46.2, R50.2
IN-9: J29.3, U16.2
unnamed: C1.1, U2.1
unnamed: C1.2, R5.2
unnamed: C2.1, U3.1
unnamed: C2.2, R6.2
unnamed: C3.1, R8.1
unnamed: C8.1, R4.2, R10.1, R11.2, U4.4
unnamed: C16.1, R10.2, U7.1
unnamed: C16.2, R12.2
unnamed: C19.1, R15.1, U8.1
unnamed: C19.2, R19.2
unnamed: C20.1, R14.1, R18.2
unnamed: C20.2, J10.1, JP22.1, R23.2, U9.1
unnamed: C21.2, R18.1, U9.3
unnamed: C22.1, R17.1, R20.2
unnamed: C22.2, JP23.1, R25.2, TP6.1, U10.1
unnamed: C23.2, R20.1, U10.3
unnamed: C28.1, R26.1
unnamed: C28.2, JP18.2, R24.2, TP5.1
unnamed: C31.2, J9.1, JP21.1, R26.2
unnamed: C32.1, JP23.2, TP7.1
unnamed: C32.2, C33.2, R27.2
unnamed: C33.1, R28.2, U11.3
unnamed: C39.1, U14.2
unnamed: C39.2, U14.4
unnamed: C43.1, C45.1, R33.2, U14.5, U15.2, U15.3
unnamed: C50.1, U15.4
unnamed: C58.1, U16.1
unnamed: C58.2, R34.2
unnamed: C62.1, R35.1, R36.2
unnamed: C62.2, J28.1, JP30.1, R42.2, U17.1
unnamed: C65.2, R36.1, U17.3
unnamed: C67.2, R47.1, R49.2
unnamed: C68.1, M1.5, R48.1
unnamed: C68.2, M1.4
unnamed: C69.2, M1.7, R49.1
unnamed: C70.1, M1.20, R56.2
unnamed: C70.2, M1.1
unnamed: C72.1, M1.18, R54.2, R55.2
unnamed: C73.1, JP27.2, JP29.1, R57.2, TP10.1
unnamed: C73.2, JP28.2, R56.1
unnamed: C75.1, R59.2, R62.1, R64.1
unnamed: C75.2, R60.2, R61.1, R63.1
unnamed: C76.1, U18.2
unnamed: C77.1, R64.2, R66.1, U18.4
unnamed: C77.2, R62.2, U18.1
unnamed: C78.1, R63.2, R65.2, U18.5
unnamed: C78.2, R61.2, U18.8
unnamed: C79.1, J30.1, R65.1
unnamed: C79.2, J30.2, R66.2
unnamed: D5.2, R40.2
unnamed: J1.1, JP3.2
unnamed: J1.2, JP7.1, JP9.1, JP11.1, JP12.1, JP14.1, TP14.1
unnamed: J1.3, JP1.1, JP2.1, JP4.1, JP5.1, JP6.1, TP9.1
unnamed: J2.1, JP8.2
unnamed: J8.1, JP20.1, U8.6
unnamed: J11.1, JP24.1, R27.1, R30.2, U11.1
unnamed: J31.1, JP30.2, R60.1
unnamed: JP3.1, R1.2
unnamed: JP10.2, JP13.2, JP15.2, R1.1
unnamed: JP16.1, TP1.1, U3.6
unnamed: JP16.2, R14.2, TP3.1
unnamed: JP17.1, TP2.1, U2.6
unnamed: JP17.2, R17.2, TP4.1
unnamed: JP18.1, U7.6
unnamed: JP25.1, TP15.1, U16.6
unnamed: JP25.2, R35.2, TP16.1
unnamed: JP26.2, R45.1, R46.1
unnamed: JP27.1, R47.2, TP11.1
unnamed: JP28.1, M1.19, TP13.1
unnamed: JP29.2, M1.6
unnamed: M1.2, R50.1
unnamed: M1.3, R51.1
unnamed: M1.9, R52.2, R53.1
unnamed: R5.1, U2.8
unnamed: R6.1, U3.8
unnamed: R7.2, R8.2, R9.2, U1.4
unnamed: R9.1, U6.1, U6.4
unnamed: R11.1, R12.1, U7.8
unnamed: R15.2, R16.1, U6.3
unnamed: R16.2, R19.1, U8.8
unnamed: R21.2, U9.4
unnamed: R22.2, U10.4
unnamed: R29.2, U11.4
unnamed: R32.2, R33.1, U14.7
unnamed: R34.1, U16.8
unnamed: R41.2, U17.4
unnamed: R58.2, U14.6
OFFSET_AD8232: IC1.11, J13.1
PWDN: IC1.35, J18.2, R38.2
REF_OUT_AD8232: C69.1, J6.1, JP8.3, JP26.3, M1.8, R52.1, R57.1
RESET: IC1.36, J18.3, R37.2
RLD1: C8.2, JP13.1, R4.1, U4.1
RLD2: C3.2, JP10.1, R7.1, U1.1
RLDIN1: IC1.62, J12.2
RLDINV: C40.2, IC1.61, J12.3, R31.1
RLDOUT1: C40.1, IC1.63, J12.1, JP15.1, R31.2
RLD_REF1: IC1.60, J12.4
SCLK: IC1.40, J17.4, J27.4
START: IC1.38, J16.1, J26.1, R44.1
VCAP1_1: C57.1, IC1.28
VCAP2_1: C56.1, IC1.30
VCAP3_1: C51.1, C53.1, IC1.55
VCAP4_1: C49.1, IC1.26
VREFP1: C54.1, C55.1, IC1.25, TP8.1
WTC_1: C61.1, IC1.64

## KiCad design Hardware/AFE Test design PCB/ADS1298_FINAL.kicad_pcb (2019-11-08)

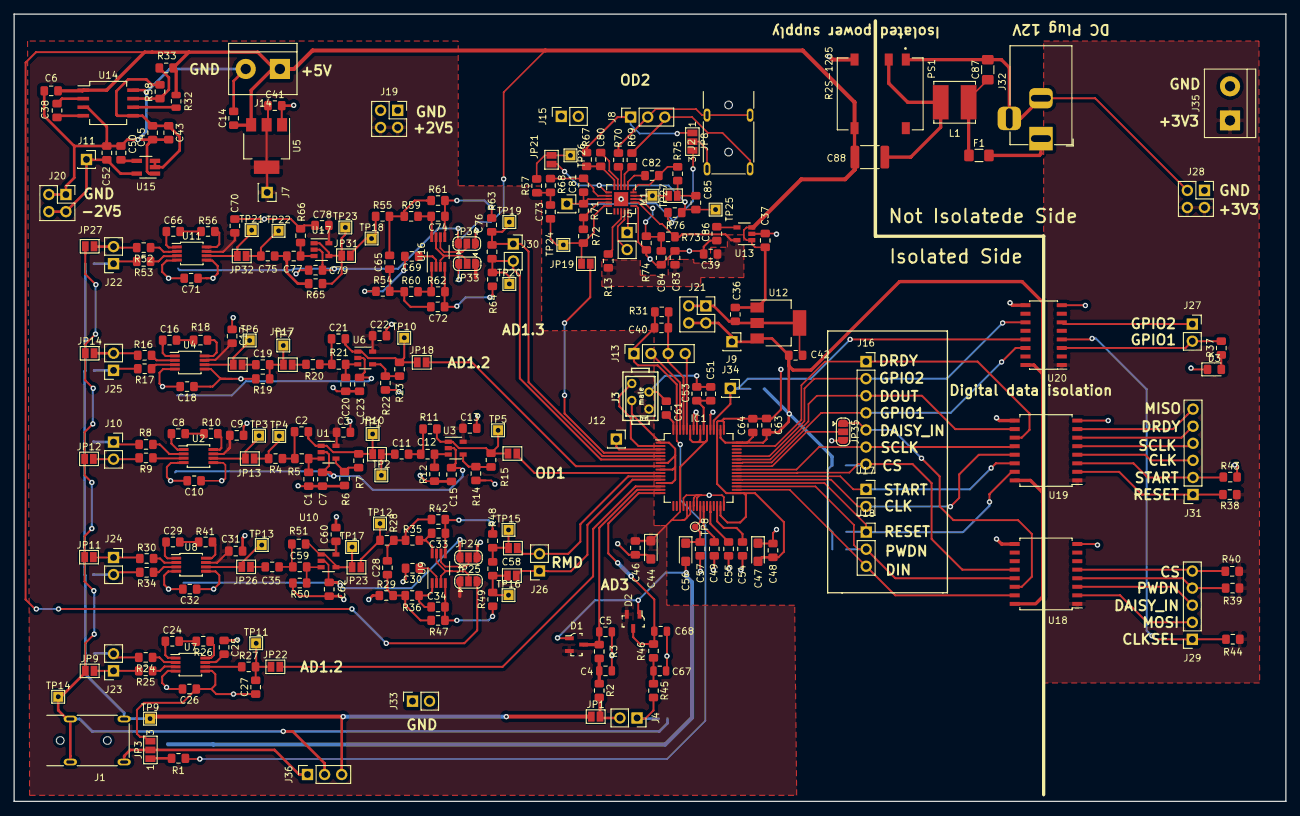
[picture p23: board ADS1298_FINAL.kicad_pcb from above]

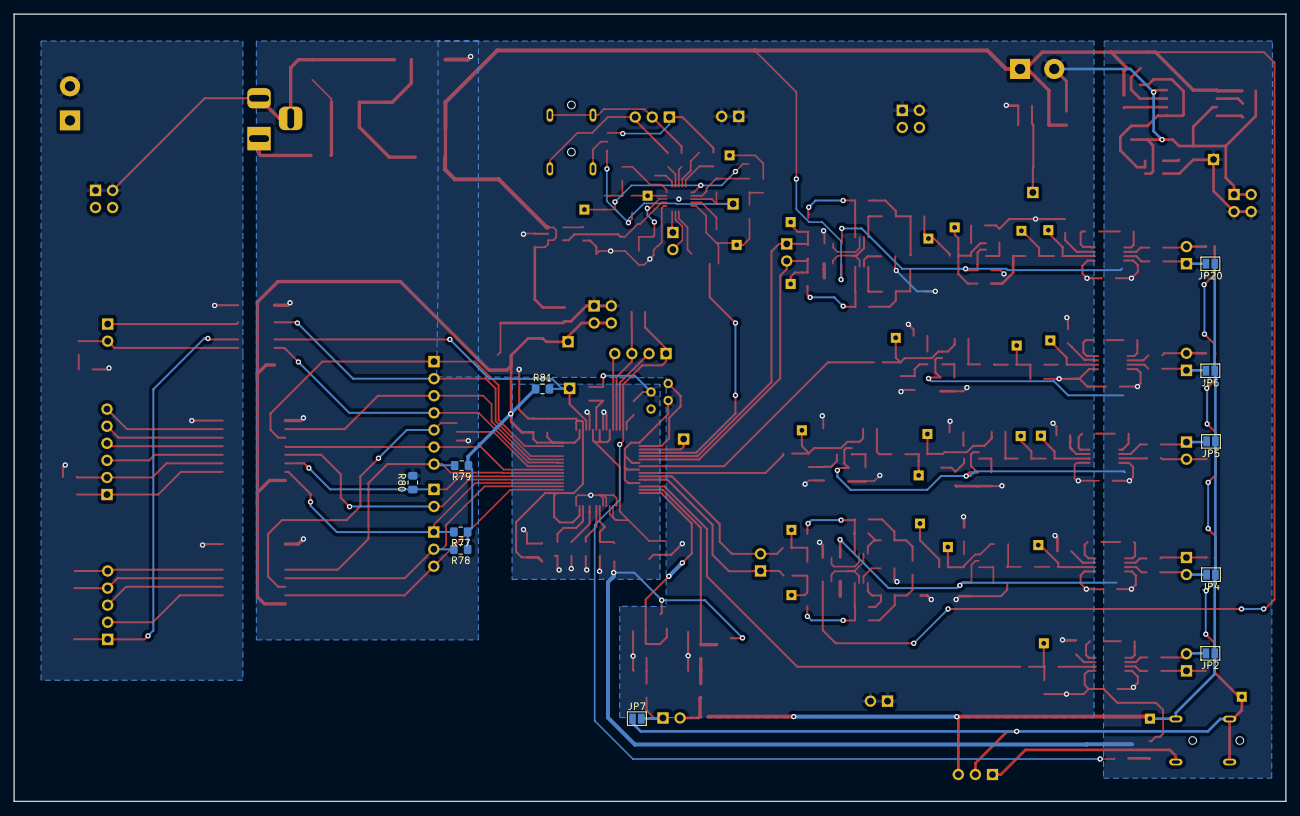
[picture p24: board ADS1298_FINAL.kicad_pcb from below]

Board: 2 copper layers, 189.0 x 117.0 mm, 295 parts (11 on the bottom side), 187 nets.

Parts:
C1, C2, C20, C21, C35, C59, C75, C77: 4.7nF; C_0805_2012Metric_Pad1.15x1.40mm_HandSolder
C3, C7, C9, C10, C13, C15, C17, C18, C19, C22, C23, C25, C26, C27, C28, C30, C31, C32, C33, C34, C58, C60, C62, C65, C69, C70, C71, C72, C74, C76, C78, C79: 100n; C_0805_2012Metric_Pad1.15x1.40mm_HandSolder
C4, C5, C67, C68: 47pF; C_0805_2012Metric
C6, C43: 4.7uF; C_0805_2012Metric_Pad1.15x1.40mm_HandSolder
C8, C16, C24, C29: 10uF; C_0805_2012Metric_Pad1.15x1.40mm_HandSolder
C11, C12, C50, C86: 10nF; C_0805_2012Metric_Pad1.15x1.40mm_HandSolder
C14, C36, C37, C38, C41, C42, C49, C51, C54, C64, C66: 1uF; C_0805_2012Metric_Pad1.15x1.40mm_HandSolder
C39, C45, C52: 2.2uF; C_0805_2012Metric_Pad1.15x1.40mm_HandSolder
C40: 1M; C_0805_2012Metric_Pad1.15x1.40mm_HandSolder
C44: 10uF; CP_EIA-3216-12_Kemet-S
C46, C48, C57: 0.1u; C_0805_2012Metric_Pad1.15x1.40mm_HandSolder
C47, C56: 10uF; CP_EIA-3216-10_Kemet-I
C53: .1uF; C_0805_2012Metric_Pad1.15x1.40mm_HandSolder
C55: 22uF; C_0805_2012Metric_Pad1.15x1.40mm_HandSolder
C61, C73, C80, C81: 1nF; C_0805_2012Metric_Pad1.15x1.40mm_HandSolder
C63: 0.1uF; C_0805_2012Metric_Pad1.15x1.40mm_HandSolder
C82, C85: 4700nF; C_0805_2012Metric_Pad1.15x1.40mm_HandSolder
C83, C84: 100nF; C_0805_2012Metric_Pad1.15x1.40mm_HandSolder
C87: 2.2uF; C_1206_3216Metric_Pad1.42x1.75mm_HandSolder
C88: 470pF; Fuse_1812_4532Metric_Pad1.30x3.40mm_HandSolder
D1, D2: D_Schottky_x2_Serial_AKC; SOT-23-3
D3: LED; LED_0805_2012Metric_Pad1.15x1.40mm_HandSolder
F1: Fuse; Fuse_1206_3216Metric_Pad1.42x1.75mm_HandSolder
IC1: ADS1298_By_Oliver; TQFP-64_10x10mm_P0.5mm
J1, J2: AUDIO_JACK_By_OLIVER; MX387GL
J3: external header 2; 0-215464-4_TH_4-pin_male
J4, J5, J10, J15, J17, J22, J23, J24, J25, J26, J27, J30, J33: Conn_01x02; PinSocket_1x02_P2.54mm_Vertical
J6, J7, J9, J11, J12, J34: Conn_01x01; PinSocket_1x01_P2.54mm_Vertical
J8, J18, J36: Conn_01x03; PinSocket_1x03_P2.54mm_Vertical
J13: Conn_01x04; PinSocket_1x04_P2.54mm_Vertical
J14, J35: Screw_Terminal_01x02; TerminalBlock_bornier-2_P5.08mm
J16: Conn_01x07; PinSocket_1x07_P2.54mm_Vertical
J19, J20, J21, J28: Conn_02x02_Counter_Clockwise; PinSocket_2x02_P2.54mm_Vertical
J29: Conn_01x05; PinSocket_1x05_P2.54mm_Vertical
J31: Conn_01x06; PinSocket_1x06_P2.54mm_Vertical
J32: Barrel_Jack_Switch; BarrelJack_Horizontal
JP1, JP2, JP4, JP5, JP6, JP7, JP9, JP11, JP12, JP14, JP19, JP20, JP27: SolderJumper_2_Open; SolderJumper-2_P1.3mm_Open_Pad1.0x1.5mm
JP3, JP8: Jumper_3_Open; SolderJumper-3_P1.3mm_Open_Pad1.0x1.5mm_NumberLabels
JP10, JP13, JP15, JP16, JP17, JP18, JP22, JP23, JP26, JP28, JP30, JP31, JP32: Jumper; SolderJumper-2_P1.3mm_Open_Pad1.0x1.5mm
JP21, JP29: Jumper_2_Open; SolderJumper-2_P1.3mm_Open_Pad1.0x1.5mm
JP24, JP25, JP33, JP34, JP35: Jumper_3_Open; SolderJumper-3_P1.3mm_Open_RoundedPad1.0x1.5mm
L1: 10uH; L_Bourns_SRN6045TA
M1: AD8232; LFCSP-20-1EP_4x4mm_P0.5mm_EP2.1x2.1mm
PS1: R2S-1205; CONV_R2S-1205
R1, R8, R9, R16, R17, R24, R25, R30, R33, R34, R52, R53: 100k; R_0805_2012Metric_Pad1.15x1.40mm_HandSolder
R2, R3, R45, R46: 2.1k; R_0805_2012Metric_Pad1.15x1.40mm_HandSolder
R4: 47k; R_0805_2012Metric_Pad1.15x1.40mm_HandSolder
R5: 91k; R_0805_2012Metric_Pad1.15x1.40mm_HandSolder
R6, R39, R78: 10K; R_0805_2012Metric_Pad1.15x1.40mm_HandSolder
R7, R13, R14, R15, R22, R38, R43, R44, R71, R77, R80, R81: 10k; R_0805_2012Metric_Pad1.15x1.40mm_HandSolder
R10, R18, R26, R41: 1300R; R_0805_2012Metric_Pad1.15x1.40mm_HandSolder
R11: 1.8M; R_0805_2012Metric_Pad1.15x1.40mm_HandSolder
R12: 1.3M; R_0805_2012Metric_Pad1.15x1.40mm_HandSolder
R19, R27, R37: 1K; R_0805_2012Metric_Pad1.15x1.40mm_HandSolder
R20, R50: 36k; R_0805_2012Metric_Pad1.15x1.40mm_HandSolder
R21, R28, R29, R35, R36, R42, R47, R48, R49, R51, R54, R55, R59, R60, R61, R62, R63, R64: 130k; R_0805_2012Metric_Pad1.15x1.40mm_HandSolder
R23, R72: 30k; R_0805_2012Metric_Pad1.15x1.40mm_HandSolder
R31: 1.5nF; R_0805_2012Metric_Pad1.15x1.40mm_HandSolder
R32: 10k; R_0805_2012Metric
R40, R79: 100K; R_0805_2012Metric_Pad1.15x1.40mm_HandSolder
R56: 20k; R_0805_2012Metric_Pad1.15x1.40mm_HandSolder
R57: 160k; R_0805_2012Metric_Pad1.15x1.40mm_HandSolder
R58: 50k; R_0805_2012Metric_Pad1.15x1.40mm_HandSolder
R65, R66: R; R_0805_2012Metric_Pad1.15x1.40mm_HandSolder
R67: 390k; R_0805_2012Metric_Pad1.15x1.40mm_HandSolder
R68: 620k; R_0805_2012Metric_Pad1.15x1.40mm_HandSolder
R69, R70: 180k; R_0805_2012Metric_Pad1.15x1.40mm_HandSolder
R73, R74: 10M; R_0805_2012Metric_Pad1.15x1.40mm_HandSolder
R75: 340k; R_0805_2012Metric_Pad1.15x1.40mm_HandSolder
R76: 3.4k; R_0805_2012Metric_Pad1.15x1.40mm_HandSolder
TP1, TP2, TP3, TP4, TP5, TP6, TP7, TP9, TP10, TP11, TP12, TP13, TP14, TP15, TP16, TP17, TP18, TP19, TP20, TP21, TP22, TP23, TP24, TP25, TP26, TP27: TestPoint; TestPoint_THTPad_1.5x1.5mm_Drill0.7mm
TP8: TestPoint; TestPoint_Pad_D1.0mm
U1, U3, U6, U10, U17: OPA333xxDBV; SOT-23-5
U2, U4, U7, U8, U11: INA333AIDGKR; MSOP-8_3x3mm_P0.65mm
U5: TLV1117-25; SOT-223-3_TabPin2
U9, U16: THS4521IDGKT; VSSOP-8_3.0x3.0mm_P0.65mm
U12: MCP1825S; SOT-223-3_TabPin2
U13: LP2985-3.5; SOT-23-5
U14: MAX889T; SO-8_5.3x6.2mm_P1.27mm
U15: TPS72325; SOT-23-5_HandSoldering
U18, U19: Si8662; SOIC-16W_7.5x10.3mm_P1.27mm
U20: Si8606; SOIC-16_3.9x9.9mm_P1.27mm

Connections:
+2V5: C3.1, C9.2, C13.1, C17.2, C22.1, C25.2, C31.2, C41.1, C44.1, C46.1, C60.1, C70.2, C78.1, D1.2, D2.2, IC1.19, IC1.21, IC1.22, IC1.54, IC1.56, IC1.59, J3.1, J7.1, J19.3, J19.4, JP25.1, JP33.1, U1.5, U2.7, U3.5, U4.7, U5.2, U6.5, U7.7, U8.7, U10.5, U11.7, U17.5
+3V3: J28.3, J28.4, J35.1, R38.1, R39.1, R40.1, R44.1, U18.1, U19.1, U20.1
+3V5: C39.1, C83.2, M1.17, R13.2, R73.1, U13.5
+3_3V: C42.1, C63.1, C64.1, IC1.48, IC1.50, J9.1, J21.3, J21.4, R77.1, R78.1, R79.1, R81.1, U12.3, U18.16, U19.16, U20.16
+5V: C6.1, C14.1, C36.1, C37.1, C88.1, J14.1, JP25.3, JP33.3, PS1.5, R32.1, R33.1, U5.3, U12.1, U13.1, U13.3, U14.1
-2V5: C7.2, C10.2, C15.1, C18.2, C23.1, C26.2, C32.2, C47.1, C48.1, C49.2, C51.2, C52.1, C53.2, C54.2, C55.2, C56.2, C57.2, C61.2, C62.1, C71.2, C79.1, D1.1, D2.1, IC1.20, IC1.23, IC1.24, IC1.32, IC1.53, IC1.57, IC1.58, J3.3, J11.1, J20.3, J20.4, JP24.1, JP34.1, U1.2, U2.4, U3.2, U4.4, U6.2, U7.4, U8.4, U10.2, U11.4, U15.5, U17.2
/Alternative Desing 1.3/low_pass_out: JP23.1, R51.1, TP17.1, U10.1, U10.4
/Original design 1/INA_OUT: JP13.2, R4.2, TP4.1
/Schematic marelini/low_pass_out_m: JP31.1, R65.1, TP23.1, U17.1, U17.4
/sheet794AF31F/EMG_OUT: C73.1, JP19.1, M1.10, R72.2, TP24.1
/sheet794AF31F/SDN_MCU: M1.13, R13.1
AD-DC1: J5.2, M1.14
AGND: C87.2, D3.1, J28.1, J28.2, J32.2, J32.3, J35.2, PS1.1, R43.2, U18.8, U19.8, U20.8
CLK: IC1.37, J17.2, U19.13
CLKSEL: IC1.52, J34.1, R81.2, U20.13
CLKSEL_ISO: J29.1, R44.2, U20.4
CLK_ISO: J31.3, U19.4
CS: IC1.39, J16.7, R79.2, U18.12
CS_ISO: J29.5, R40.2, U18.5
DAISY_CON_1: J16.5, JP35.1, U18.14
DAISY_CON_1_ISO: J29.3, U18.3
DGND: C1.1, C3.2, C4.2, C5.2, C6.2, C7.1, C9.1, C10.1, C13.2, C14.2, C15.2, C17.1, C18.1, C20.1, C22.2, C23.2, C25.1, C26.1, C27.1, C30.2, C31.1, C32.1, C36.2, C37.2, C39.2, C41.2, C42.2, C43.2, C44.2, C45.2, C46.2, C47.2, C48.2, C50.2, C52.2, C60.2, C62.2, C63.2, C64.2, C67.2, C68.2, C69.2, C70.1, C71.1, C78.2, C79.2, C83.1, C84.2, C86.2, IC1.1, IC1.7, IC1.9, IC1.13, IC1.31, IC1.33, IC1.49, IC1.51, J3.2, J14.2, J15.1, J15.2, J19.1, J19.2, J20.1, J20.2, J21.1, J21.2, J33.1, J33.2, JP3.3, JP24.3, JP34.3, JP35.3, M1.16, M1.21, PS1.4, R6.1, R12.1, R14.1, R19.2, R22.1, R29.1, R50.1, R54.1, R66.2, R74.1, R80.2, U2.5, U4.5, U5.1, U7.5, U8.5, U11.5, U12.2, U13.2, U14.3, U14.8, U15.1, U18.9, U19.9, U20.9
DIN: IC1.34, J18.3, U18.15
DOUT: IC1.43, J16.3, U19.10
DRDY: IC1.47, J16.1, U19.11
DRDY_ISO: J31.5, U19.6
DRL3: J8.1, JP8.1, R67.2
FR1: J5.1, M1.15
GPIO_1: IC1.42, J16.4, U20.14
GPIO_1_ISO: J27.2, R37.2, U20.3
GPIO_2: IC1.44, J16.2, U20.11
GPIO_2_ISO: J27.1, U20.6
IN1N: C68.1, D2.3, IC1.16, R46.1
IN1NI: J4.1, JP7.2, R45.2
IN1P: C5.1, D1.3, IC1.15, R3.1
IN1PI: J4.2, JP1.2, R2.2
IN2: IC1.14, JP22.2
IN3N: IC1.11, J26.2, JP28.2
IN3P: IC1.12, J26.1, JP30.1
IN4: IC1.10, JP15.2
IN5: IC1.8, JP18.2
IN6N: C76.2, IC1.6, J30.2, R64.2, TP20.1
IN6P: C76.1, IC1.5, J30.1, R63.1, TP19.1
IN7: IC1.4, JP19.2
IN8: IC1.2, J3.4
IN+2: J23.2, JP2.2, R24.2
IN+3: J24.2, JP4.2, R34.2
IN+4: J10.1, JP5.2, R8.2
IN+5: J25.1, JP6.2, R17.2
IN+8: J2.2, J8.2, R70.2
IN+9: J22.1, JP20.2, R53.2
IN-2: J23.1, JP9.2, R25.2
IN-3: J24.1, JP11.2, R30.2
IN-4: J10.2, JP12.2, R9.2
IN-5: J25.2, JP14.2, R16.2
IN-8: J2.3, J8.3, R69.2
IN-9: J22.2, JP27.2, R52.2
MISO_ISO: J31.6, U19.7
MOSI_ISO: J29.2, U18.2
unnamed: C1.2, R5.1, U1.3
unnamed: C2.1, R4.1, R5.2
unnamed: C2.2, JP10.1, R7.2, TP1.1, U1.1
unnamed: C4.1, R2.1, R3.2
unnamed: C8.1, U2.1
unnamed: C8.2, R10.2
unnamed: C11.1, JP10.2, TP2.1
unnamed: C11.2, C12.2, R11.2
unnamed: C12.1, R12.2, U3.3
unnamed: C16.1, U4.1
unnamed: C16.2, R18.2
unnamed: C19.1, JP16.2
unnamed: C19.2, JP17.1, R19.1, TP7.1
unnamed: C20.2, R21.1, U6.3
unnamed: C21.1, R20.1, R21.2
unnamed: C21.2, JP18.1, R23.2, TP10.1, U6.1
unnamed: C24.1, U7.1
unnamed: C24.2, R26.2
unnamed: C27.2, JP22.1, R27.2, TP11.1
unnamed: C28.1, R29.2, R36.1, R47.1
unnamed: C28.2, R28.2, R35.1, R42.1
unnamed: C29.1, U8.1
unnamed: C29.2, R41.2
unnamed: C30.1, U9.2
unnamed: C33.1, R42.2, R48.2, U9.5
unnamed: C33.2, R35.2, U9.8
unnamed: C34.1, R47.2, R49.1, U9.4
unnamed: C34.2, R36.2, U9.1
unnamed: C35.1, JP26.2
unnamed: C35.2, C59.1, R51.2
unnamed: C38.1, U14.2
unnamed: C38.2, U14.4
unnamed: C43.1, C45.1, R58.2, U14.5, U15.2, U15.3
unnamed: C50.1, U15.4
unnamed: C58.1, JP28.1, R48.1, TP15.1
unnamed: C58.2, JP30.2, R49.2, TP16.1
unnamed: C59.2, R50.2, U10.3
unnamed: C65.1, R54.2, R60.1, R62.1
unnamed: C65.2, R55.2, R59.1, R61.1
unnamed: C66.1, U11.1
unnamed: C66.2, R56.2
unnamed: C67.1, R45.1, R46.2
unnamed: C69.1, U16.2
unnamed: C72.1, R62.2, R64.1, U16.4
unnamed: C72.2, R60.2, U16.1
unnamed: C73.2, R57.1, R68.2
unnamed: C74.1, R61.2, R63.2, U16.5
unnamed: C74.2, R59.2, U16.8
unnamed: C75.1, JP32.2, TP22.1
unnamed: C75.2, C77.1, R65.2
unnamed: C77.2, R66.1, U17.3
unnamed: C80.1, M1.5, R67.1
unnamed: C80.2, M1.4
unnamed: C81.2, M1.7, R68.1
unnamed: C82.1, M1.20, R75.2
unnamed: C82.2, M1.1
unnamed: C84.1, M1.18, R73.2, R74.2
unnamed: C85.1, JP21.2, M1.6, R76.2, TP25.1
unnamed: C85.2, JP29.2, R75.1
unnamed: C86.1, U13.4
unnamed: C87.1, F1.1, L1.1
unnamed: C88.2, L1.2, PS1.2
unnamed: D3.2, R37.1
unnamed: F1.2, J32.1
unnamed: IC1.41, JP35.2
unnamed: J1.1, J36.1, JP3.2
unnamed: J1.2, J36.2, JP7.1, JP9.1, JP11.1, JP12.1, JP14.1, JP27.1, TP14.1
unnamed: J1.3, J36.3, JP1.1, JP2.1, JP4.1, JP5.1, JP6.1, JP20.1, TP9.1
unnamed: J2.1, JP8.2
unnamed: JP3.1, R1.2
unnamed: JP13.1, TP3.1, U2.6
unnamed: JP15.1, R11.1, R15.2, TP5.1, U3.1
unnamed: JP16.1, TP6.1, U4.6
unnamed: JP17.2, R20.2
unnamed: JP21.1, R57.2, TP26.1
unnamed: JP23.2, R28.1, TP12.1
unnamed: JP24.2, U9.6
unnamed: JP25.2, U9.3, U9.7
unnamed: JP26.1, TP13.1, U8.6
unnamed: JP29.1, M1.19, TP27.1
unnamed: JP31.2, R55.1, TP18.1
unnamed: JP32.1, TP21.1, U11.6
unnamed: JP33.2, U16.3, U16.7
unnamed: JP34.2, U16.6
unnamed: M1.2, R69.1
unnamed: M1.3, R70.1
unnamed: M1.9, R71.2, R72.1
unnamed: R6.2, R7.1, U1.4
unnamed: R8.1, U2.2
unnamed: R9.1, U2.3
unnamed: R10.1, U2.8
unnamed: R14.2, R15.1, U3.4
unnamed: R16.1, U4.2
unnamed: R17.1, U4.3
unnamed: R18.1, U4.8
unnamed: R22.2, R23.1, U6.4
unnamed: R24.1, U7.2
unnamed: R25.1, U7.3
unnamed: R26.1, U7.8
unnamed: R27.1, U7.6
unnamed: R30.1, U8.2
unnamed: R32.2, U14.6
unnamed: R33.2, R58.1, U14.7
unnamed: R34.1, U8.3
unnamed: R41.1, U8.8
unnamed: R52.1, U11.2
unnamed: R53.1, U11.3
unnamed: R56.1, U11.8
OFFSET_AD8232: IC1.3, J12.1
PWDN: IC1.35, J18.2, R78.2, U18.13
PWDN_ISO: J29.4, R39.2, U18.4
REF_OUT_AD8232: C81.1, J6.1, JP8.3, M1.8, R71.1, R76.1
RESET: IC1.36, J18.1, R77.2, U19.15
RESET_ISO: J31.1, R38.2, U19.2
RLDIN1: IC1.62, J13.2
RLDINV: C40.2, IC1.61, J13.3, R31.1
RLDOUT1: C40.1, IC1.63, J13.1, R1.1, R31.2
RLD_REF1: IC1.60, J13.4
SCLK: IC1.40, J16.6, U19.12
SCLK_ISO: J31.4, U19.5
START: IC1.38, J17.1, R80.1, U19.14
START_ISO: J31.2, R43.1, U19.3
VCAP1_1: C55.1, IC1.28
VCAP2_1: C54.1, IC1.30
VCAP3_1: C51.1, C53.1, IC1.55
VCAP4_1: C49.1, IC1.26
VREFP1: C56.1, C57.1, IC1.25, TP8.1
WTC_1: C61.1, IC1.64

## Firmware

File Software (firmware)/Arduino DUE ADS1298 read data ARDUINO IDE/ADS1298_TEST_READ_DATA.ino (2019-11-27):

#include <SPI.h>  // include the SPI library:
#include "Arduino.h"
#include <string.h>

#if defined(__SAM3X8E__)
  #define isDUE  //Detect Arduino Due
  #define WiredSerial SerialUSB //Use Due's Native port
#else  
  #define WiredSerial Serial
#endif

#define BAUD_RATE 2000000     // WiredSerial ignores this and uses the maximum rate

// system commands
#define  WAKEUP 0x02
#define  STANDBY 0x04
#define  RESET 0x06
#define START 0x08
#define STOP 0x0A

// read commands
#define RDATAC 0x10
#define SDATAC 0x11
#define RDATA  0x12

// register commands
#define RREG 0x20
#define WREG 0x40

//Register Addresses
#define ID 0x00
#define CONFIG1 0x01
#define CONFIG2 0x02
#define CONFIG3 0x03
#define LOFF 0x04
#define CH1SET 0x05
#define CH2SET 0x06
#define CH3SET 0x07
#define CH4SET 0x08
#define CH5SET 0x09
#define CH6SET 0x0A
#define CH7SET 0x0B
#define CH8SET 0x0C
#define BIAS_SENSP 0x0D
#define BIAS_SENSN 0x0E
#define LOFF_SENSP 0x0F
#define LOFF_SENSN 0x10
#define LOFF_FLIP 0x11
#define LOFF_STATP 0x12
#define LOFF_STATN 0x13
#define GPIO 0x14
#define MISC1 0x15
#define MISC2 0x16
#define CONFIG4 0x17

uint8_t data[27];
uint32_t data1[8];

int32_t channelData [50];  // array used when reading channel data board 1+2
uint8_t DataToSend[40]; //
uint8_t MessageCounter = 0;
uint8_t MessageLength = 0;

//constants define pins on Arduino 
// const int IPIN_PWDN = 2; //not required for TI demo kit
//const int PIN_CLKSEL = 6;//6;//*optional
const int IPIN_RESET  = 3;//*optional
const int PIN_START = 4;
const int IPIN_DRDY = 5;
const int PIN_PWD = 2;

const int IPIN_CS = 10;//10

int gMaxChan = 0; //maximum number of channels supported by ads129n = 4,6,8
int gIDval = 0; //Device ID : lower 5 bits of  ID Control Register 

int activeSerialPort = 0; //data will be sent to serial port that last sent commands. E.G. bluetooth or USB port
const int kPIN_LED = 13;//pin with in-built light - typically 13, 11 for Teensy 2.0. 

void adc_send_command(int cmd);
void adc_wreg(int reg, int val);
byte adc_rreg(int reg);
void readid();
void ADS1298_INIT();
void READ_DATA();

void printregister(uint8_t registernr);

void setup(){

  pinMode(IPIN_CS, OUTPUT);
  pinMode(PIN_START, OUTPUT);
  pinMode(PIN_PWD, OUTPUT);
  
  pinMode(IPIN_DRDY, INPUT);
  //pinMode(PIN_CLKSEL, OUTPUT);//*optional
  pinMode(IPIN_RESET, OUTPUT);//*optional
  //pinMode(IPIN_PWDN, OUTPUT);//*optional
  //start small peripheral interface
  pinMode(kPIN_LED, OUTPUT); 
  
  delay(100);
  
  digitalWrite(IPIN_RESET, HIGH);
  digitalWrite(PIN_PWD, HIGH);
  
  SPI.begin();
  SPI.setBitOrder(MSBFIRST);
  SPI.setClockDivider(21); 
  SPI.setDataMode(SPI_MODE1);

  //start serial port
  WiredSerial.begin(BAUD_RATE);; //use native port on Due
  while (WiredSerial.read() >= 0) {} //http://forum.arduino.cc/index.php?topic=134847.0
  //while (!WiredSerial) ; //required by Leonardo http://arduino.cc/en/Serial/IfSerial (ads129n requires 3.3v signals, Leonardo is 5v)

  delay(10000);
  readid();
  delay(500);
  readid();
  delay(500);
  readid();
  delay(500);
  readid();
  delay(500);
  readid();
  delay(8000);
  ADS1298_INIT();
}

void loop()
{
  //readid(); delay(100);
  //ADS1298_INIT();
  //
  //digitalWrite(PIN_START, LOW);
  //detachInterrupt(digitalPinToInterrupt(IPIN_DRDY));
}

void adc_send_command(int cmd)
{
  digitalWrite(IPIN_CS, LOW);
  SPI.transfer(cmd);
  delayMicroseconds(1);
  digitalWrite(IPIN_CS, HIGH);
}

void adc_wreg(int reg, int val)
{
  //see pages 40,43 of datasheet - 
  digitalWrite(IPIN_CS, LOW);
  SPI.transfer(WREG |reg);
  SPI.transfer(0);  // number of registers to be read/written – 1
  SPI.transfer(val);
  delayMicroseconds(1);
  digitalWrite(IPIN_CS, HIGH);
}

byte adc_rreg(int reg)
{
  byte val;
  digitalWrite(IPIN_CS, LOW);
  SPI.transfer(RREG | reg);
  SPI.transfer(0);  // number of registers to be read/written
  val = SPI.transfer(0);
  delayMicroseconds(1);
  digitalWrite(IPIN_CS, HIGH);
  return val;
}

void readid()
{
  delay(500); //wait for the ads129n to be ready - it can take a while to charge caps
  adc_send_command(SDATAC); // Send SDATAC Command (Stop Read Data Continuously mode)
  delayMicroseconds(100);
  //adc_send_command(STOPAC); 
  //delayMicroseconds(10);
  gIDval = adc_rreg(ID); //lower 5 bits of register 0 reveal chip type
  WiredSerial.write("Device ID: 0x"); SerialUSB.println(gIDval, HEX);
  //delay(500); 
}

void printregister(uint8_t registernr)
{
  uint8_t regvalue;
  
  regvalue = adc_rreg(registernr); //lower 5 bits of register 0 reveal chip type
  WiredSerial.write("Reg value = 0x"); SerialUSB.println(regvalue, HEX);
}

void ADS1298_INIT()
{
  delay(500); //wait for the ads129n to be ready - it can take a while to charge caps
  digitalWrite(IPIN_RESET, LOW);
  delay(1); // actually only needs 1 microsecond, we'll go with milli
  digitalWrite(IPIN_RESET, HIGH);
  delay(500);
  
  adc_send_command(SDATAC);
  delay(100);
  
  adc_wreg(CONFIG3,0xC0);
  delay(500);
  
  adc_wreg(CONFIG1,0x04); // 0x06 = 250sps, 0x05 = 500Sps, 0x04 = 1000Sps, 0x03 = 2000Sps
  delay(500);

  adc_wreg(CH1SET,0x10); // ch1 normal operation, gain 1, normal electrode input
  delay(500);  
  adc_wreg(CH2SET,0x10); // CH2 power down, gian 1, input shorted
  delay(500);
  adc_wreg(CH3SET,0x10); // CH2 power down, gian 1, input shorted
  delay(500);
  adc_wreg(CH4SET,0x91); // CH2 power down, gian 1, input shorted
  delay(500);
  adc_wreg(CH5SET,0x91); // CH2 power down, gian 1, input shorted
  delay(500);
  adc_wreg(CH6SET,0x91); // CH2 power down, gian 1, input shorted
  delay(500);
  adc_wreg(CH7SET,0x91); // CH2 power down, gian 1, input shorted
  delay(500);
  adc_wreg(CH8SET,0x91); // CH2 power down, gian 1, input shorted
  delay(500);
    
  adc_wreg(GPIO, 0x00);
  delay(100);
  
  digitalWrite(PIN_START, HIGH);  // start measruements
  delay(500);
  
  delay(100);
  
  adc_send_command(RDATAC);
  
  attachInterrupt(digitalPinToInterrupt(IPIN_DRDY), READ_DATA, FALLING);

}

void READ_DATA()
{
  uint8_t inByte;
  int i,j;        // iterator in loop
  for(i = 0; i < 9; i++){
    channelData[i] = 0;
  }

  digitalWrite(IPIN_CS, LOW);
  
  for(i = 0; i < 9; i++){
    for( j=0; j<3; j++){    //  read 24 bits of channel data from 1st ADS in 8 3 byte chunks
      inByte = SPI.transfer(0x00);
      channelData[i] = (channelData[i]<<8) | inByte;
    }
  }
  
  for (int i = 0; i < 9; i++) {
    if (i < 8)
    {
      WiredSerial.print(channelData[i], HEX);
      WiredSerial.print(","); 
    }
    else
    {
      WiredSerial.println(channelData[i], HEX);
    }  
  }
  digitalWrite(IPIN_CS, HIGH);
}

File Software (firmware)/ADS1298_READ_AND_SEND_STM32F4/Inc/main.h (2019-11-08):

/* USER CODE BEGIN Header */
/**
  ******************************************************************************
  * @file           : main.h
  * @brief          : Header for main.c file.
  *                   This file contains the common defines of the application.
  ******************************************************************************
  * @attention
  *
  * <h2><center>&copy; Copyright (c) 2019 STMicroelectronics.
  * All rights reserved.</center></h2>
  *
  * This software component is licensed by ST under Ultimate Liberty license
  * SLA0044, the "License"; You may not use this file except in compliance with
  * the License. You may obtain a copy of the License at:
  *                             www.st.com/SLA0044
  *
  ******************************************************************************
  */
/* USER CODE END Header */

/* Define to prevent recursive inclusion -------------------------------------*/
#ifndef __MAIN_H
#define __MAIN_H

#ifdef __cplusplus
extern "C" {
#endif

/* Includes ------------------------------------------------------------------*/
#include "stm32f4xx_hal.h"

/* Private includes ----------------------------------------------------------*/
/* USER CODE BEGIN Includes */

/* USER CODE END Includes */

/* Exported types ------------------------------------------------------------*/
/* USER CODE BEGIN ET */

/* USER CODE END ET */

/* Exported constants --------------------------------------------------------*/
/* USER CODE BEGIN EC */

/* USER CODE END EC */

/* Exported macro ------------------------------------------------------------*/
/* USER CODE BEGIN EM */

/* USER CODE END EM */

/* Exported functions prototypes ---------------------------------------------*/
void Error_Handler(void);

/* USER CODE BEGIN EFP */

/* USER CODE END EFP */

/* Private defines -----------------------------------------------------------*/
#define Button_Pin GPIO_PIN_0
#define Button_GPIO_Port GPIOA
#define Button_EXTI_IRQn EXTI0_IRQn
#define CS_Pin GPIO_PIN_5
#define CS_GPIO_Port GPIOC
#define CLK_SEL_Pin GPIO_PIN_12
#define CLK_SEL_GPIO_Port GPIOB
#define START_Pin GPIO_PIN_13
#define START_GPIO_Port GPIOB
#define DRDY_Pin GPIO_PIN_14
#define DRDY_GPIO_Port GPIOB
#define DRDY_EXTI_IRQn EXTI15_10_IRQn
#define RESET_Pin GPIO_PIN_15
#define RESET_GPIO_Port GPIOB
#define LED1_Pin GPIO_PIN_14
#define LED1_GPIO_Port GPIOD
/* USER CODE BEGIN Private defines */

/* USER CODE END Private defines */

#ifdef __cplusplus
}
#endif

#endif /* __MAIN_H */

/************************ (C) COPYRIGHT STMicroelectronics *****END OF FILE****/

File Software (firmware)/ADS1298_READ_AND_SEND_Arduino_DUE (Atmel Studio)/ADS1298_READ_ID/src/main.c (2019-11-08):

// Created by Oliver Kersten

#include <string.h>
#include "asf.h"
#include "stdio_serial.h"
#include "conf_board.h"
#include "conf_clock.h"
#include <string.h>

//Define GPIO pins to control ADS1298
#define CS    IOPORT_CREATE_PIN(PIOC, 29)
#define ADS_RESET    IOPORT_CREATE_PIN(PIOC, 28)
#define ADS_START    IOPORT_CREATE_PIN(PIOC, 26)

// USB CDC 
#define UDI_CDC_ENABLE_EXT(port) my_callback_cdc_enable()
extern bool my_callback_cdc_enable(void);
#define UDI_CDC_DISABLE_EXT(port) my_callback_cdc_disable()
extern void my_callback_cdc_disable(void);
#define  UDI_CDC_LOW_RATE
#define  UDI_CDC_DEFAULT_RATE             115200
#define  UDI_CDC_DEFAULT_STOPBITS         CDC_STOP_BITS_1
#define  UDI_CDC_DEFAULT_PARITY           CDC_PAR_NONE
#define  UDI_CDC_DEFAULT_DATABITS         8
#include "udi_cdc_conf.h" // At the end of conf_usb.h file

//ASD1298 control commands
#define  WAKEUP 0x02
#define  STANDBY 0x04
#define  RESET 0x06
#define START 0x08
#define STOP 0x0A

//ASD1298 read commands
#define RDATAC 0x10
#define SDATAC 0x11
#define RDATA  0x12

//ASD1298 register commands
#define RREG 0x20
#define WREG 0x40

//ASD1298 Register Addresses
#define ID 0x00
#define CONFIG1 0x01
#define CONFIG2 0x02
#define CONFIG3 0x03
#define LOFF 0x04
#define CH1SET 0x05
#define CH2SET 0x06
#define CH3SET 0x07
#define CH4SET 0x08
#define CH5SET 0x09
#define CH6SET 0x0A
#define CH7SET 0x0B
#define CH8SET 0x0C
#define BIAS_SENSP 0x0D
#define BIAS_SENSN 0x0E
#define LOFF_SENSP 0x0F
#define LOFF_SENSN 0x10
#define LOFF_FLIP 0x11
#define LOFF_STATP 0x12
#define LOFF_STATN 0x13
#define GPIO 0x14
#define MISC1 0x15
#define MISC2 0x16
#define CONFIG4 0x17

/** SPI0 MACRO definition */
#define CONF_BOARD_SPI0

/** SPI0 slave select0 MACRO definition */
#define CONF_BOARD_SPI0_NPCS0

/** Spi Hw ID . */
#define SPI_ID          ID_SPI0

#define SPI_MASTER_BASE      SPI0
#define SPI_IRQn        SPI0_IRQn

/* Chip select. */
#define SPI_CHIP_SEL 0
#define SPI_CHIP_PCS spi_get_pcs(SPI_CHIP_SEL)

/* Clock polarity & Clock phase. */
#define SPI_CLK_POLARITY 0
#define SPI_CLK_PHASE 1

/* Delay before SPCK. */
#define SPI_DLYBS 0x40

/* Delay between consecutive transfers. */
#define SPI_DLYBCT 0x10

static uint32_t gs_ul_spi_clock = 2000000;  // Set SPI CLOCK to 2MHz

uint8_t DataToSend[40]; //
uint8_t MessageCounter = 0;
uint8_t MessageLength = 0;

int32_t channelData [50];	// array used when reading channel data board 1+2

/**
 * \brief Initialize SPI as master.
 */

void spi_init(void)
{
	
	//Assign I/O lines to peripheral
	gpio_configure_pin(SPI0_MISO_GPIO, SPI0_MISO_FLAGS);
	gpio_configure_pin(SPI0_MOSI_GPIO, SPI0_MOSI_FLAGS);
	gpio_configure_pin(SPI0_SPCK_GPIO, SPI0_SPCK_FLAGS);
	gpio_configure_pin(SPI0_NPCS0_GPIO, SPI0_NPCS0_FLAGS);

	spi_enable_clock(SPI_MASTER_BASE);
	spi_disable(SPI_MASTER_BASE);
	spi_reset(SPI_MASTER_BASE);
	
	spi_set_lastxfer(SPI_MASTER_BASE);
	spi_set_master_mode(SPI_MASTER_BASE);
	spi_disable_mode_fault_detect(SPI_MASTER_BASE);
	spi_set_peripheral_chip_select_value(SPI_MASTER_BASE, SPI_CHIP_PCS);
	spi_set_clock_polarity(SPI_MASTER_BASE, SPI_CHIP_SEL, SPI_CLK_POLARITY);
	spi_set_clock_phase(SPI_MASTER_BASE, SPI_CHIP_SEL, SPI_CLK_PHASE);
	spi_set_bits_per_transfer(SPI_MASTER_BASE, SPI_CHIP_SEL,
	SPI_CSR_BITS_8_BIT);
	spi_set_baudrate_div(SPI_MASTER_BASE, SPI_CHIP_SEL,(sysclk_get_cpu_hz() / gs_ul_spi_clock));
	spi_set_transfer_delay(SPI_MASTER_BASE, SPI_CHIP_SEL, SPI_DLYBS,SPI_DLYBCT);
	spi_enable(SPI_MASTER_BASE);
}

uint8_t spi_sendrecv(uint8_t byte)
{
	uint8_t data;
	uint8_t uc_pcs;
	
	spi_write(SPI_MASTER_BASE, byte, 0, 0);
	/* Wait transfer done. */
	while ((spi_read_status(SPI_MASTER_BASE) & SPI_SR_RDRF) == 0);
	spi_read(SPI_MASTER_BASE, &data, &uc_pcs);
	return data;
}

void ADS_SEND_COMMAND(uint8_t cmd)
{
	ioport_set_pin_level(CS, IOPORT_PIN_LEVEL_LOW);		//  Open SPI
	spi_sendrecv(cmd); 		//  opcode1
	delay_us(1);
	ioport_set_pin_level(CS, IOPORT_PIN_LEVEL_HIGH);	//  close SPI
}

uint8_t ADS_RREG(uint8_t reg)
{
	uint8_t vall;
	ioport_set_pin_level(CS, IOPORT_PIN_LEVEL_LOW);
	spi_sendrecv(RREG | reg);
	spi_sendrecv(0);
	vall = spi_sendrecv(0);
	delay_us(1);
	ioport_set_pin_level(CS, IOPORT_PIN_LEVEL_HIGH);
	return vall;			//return requested register value
}

void ADS_WREG(uint8_t reg, uint8_t val)
{
	ioport_set_pin_level(CS, IOPORT_PIN_LEVEL_LOW);
	spi_sendrecv(WREG |reg);
	spi_sendrecv(0x00);
	spi_sendrecv(val);
	ioport_set_pin_level(CS, IOPORT_PIN_LEVEL_HIGH);
}

uint8_t READ_ID()
{
	uint8_t gIDval;

	delay_ms(400);
	ADS_SEND_COMMAND(SDATAC);
	delay_ms(100);
	gIDval = ADS_RREG(ID);
	delay_ms(100);

	return gIDval;
}

void ADS_updateChannelData(){
	uint8_t inByte;
	int i,j;				// iterator in loop
	for(i = 0; i < 9; i++){
		channelData[i] = 0;
	}

	ioport_set_pin_level(CS, IOPORT_PIN_LEVEL_LOW);
	
	for(i = 0; i < 9; i++){
		for( j=0; j<3; j++){		//  read 24 bits of channel data, convert into one big byte
			inByte = spi_sendrecv(0x00);
			channelData[i] = (channelData[i]<<8) | inByte;
		}
	}

	MessageLength = sprintf(DataToSend, "%02X,%02X,%02X,%02X,%02X,%02X,%02X,%02X\n\r", channelData[1],channelData[2],channelData[3],channelData[4],channelData[5],channelData[6],channelData[7],channelData[8]);
	udi_cdc_write_buf(DataToSend, MessageLength);

	ioport_set_pin_level(CS, IOPORT_PIN_LEVEL_HIGH);
}
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

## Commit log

2019-11-08 Added new files
    [1000Sps.csv, 2kSps.csv, ADS1298_FINAL-B.Cu.gbr, ADS1298_FINAL-B.Mask.gbr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]
2019-11-11 update schematic
    [ADS1298_FINAL.sch]
2019-11-21 add spatial filter
    [test1.csv, test2.csv, test3.csv]
